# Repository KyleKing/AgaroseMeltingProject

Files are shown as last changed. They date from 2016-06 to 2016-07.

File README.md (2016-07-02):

# Melting Agarose Beads for Enhanced Optical Detection

The goal of this project is to demonstrate that a bead bed of Low Melting Point Agarose beads can capture an analyte with a sandwich immunoassay and when melted, the optical improvement will enhance the detection limit.

In this folder you will find all the code, notes, and resources to help you finish this project. I learned a great deal from electronics and software to microfluidics that I would have never learned in my classes. Feel free to email me any questions [kmking72@gmail.com](mailto:kmking72@gmail.com) or [create a new issue at the private Github repository](https://github.com/KyleKing/AgaroseMeltingProject/issues/new) - note: see login details below for how to access.

I've organized and condensed my notes as concisely as possible. I would start by looking through the posters `1_Posters` to get a general idea of the project.

## How to read `.md` files:

*Summary of this [Stack Overflow answer](http://stackoverflow.com/a/15626336/3219667)*

Download the [Markdown Preview Plus](https://chrome.google.com/webstore/detail/markdown-preview-plus/febilkbfcbhebfnokafefeacimjdckgl) chrome extension. Go to the chrome extensions settings page (*chrome://extensions/*) and check the box to `Allow access to file URL's`. The last step is to go to the [Markdown Preview Plus Settings Panel](chrome-extension://febilkbfcbhebfnokafefeacimjdckgl/options.html) and change the default CSS to `github`.

### Alternatively

The entire folder is on Github under a private repository so you can more easily explore all of the files. You will need the login info for the shared Github account [UMD-MML](https://github.com/UMD-MML) (see the associated Mantis post). Once signed in, visit: https://github.com/KyleKing/AgaroseMeltingProject

# Abstract

Rapid diagnostic platforms have become increasingly necessary to address global disease outbreaks, make informed timely medical decisions, and meet the needs of resource-poor regions. Current diagnostic technology is cost prohibitive for point of care, requiring all samples to be sent to a centralized lab for analysis, which can delay results from several hours to a week. Researchers have attempted to address this issue through the development of microfluidic diagnostics that detect a variety of biomarkers. Many of these tests, however, use two-dimensional surfaces to immobilize target biomarkers, limiting detection performance. Using a three-dimensional biomarker capture matrix will increase the amount of sample fluid in contact with an activated surface by an order of magnitude. This increased contact reduces the diffusion time and leads to faster, more reliable, and more accurate diagnostic tests. Three-dimensional matrices have been considered impractical due to the highly opaque nature of the matrix. I have demonstrated a simple detection method using low melting point (LMP) agarose beads. The beads can be activated to create an exposed biotin group, which can be further activated for a sandiwch immunoassay. While conducting the assay, the agarose beads are nearly opaque; however, once the target biomarkers have been immobilized on the bead matrix, the beads can be melted into a solid mass, reducing light scattering and improving optical clarity for high diagnostic performance. To produce these beads at sufficient scale and throughput, I developed a Raspberry Pi-controlled microfluidic device to automate a scalable production method. With additional research, this novel approach can be developed for clinical applications such as tracking the spread of Ebola, Zika, or other future outbreaks.

## Where is everything?

I packed up everything into a box in the main lab (pictured below). All of the refrigerated chemicals are in the top left drawer of the main lab fridge.

<p align="center">
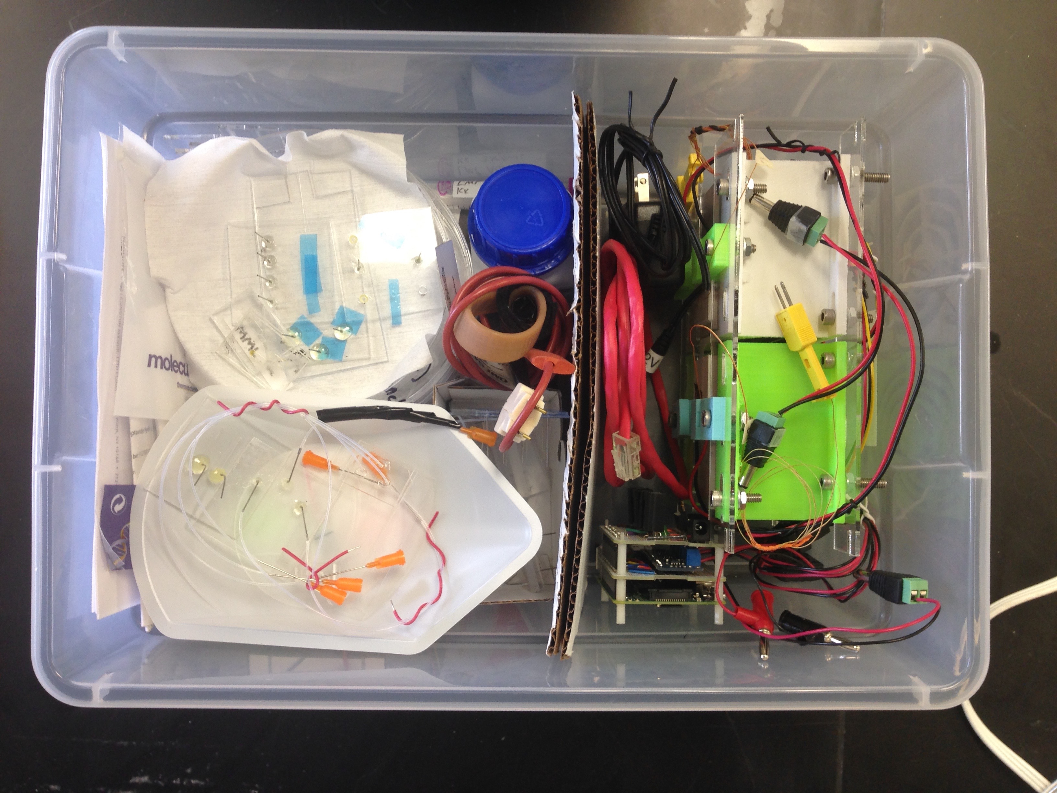
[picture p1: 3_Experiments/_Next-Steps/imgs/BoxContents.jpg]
  
</p>
<p align="center">My box contents</p>

<p align="center">
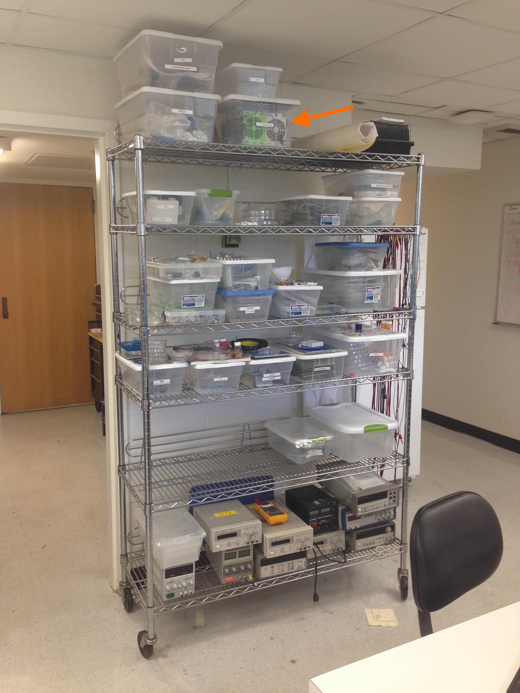
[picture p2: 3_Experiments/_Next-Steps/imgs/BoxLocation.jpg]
  
</p>
<p align="center">The box is located on the top of the shelving unit in the main lab</p>

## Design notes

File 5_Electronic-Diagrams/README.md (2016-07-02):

# Electronic Diagrams

## DIY Version:

Included is a [Fritzing](http://fritzing.org/home/) (`DualHeatStage---Breadboard-Version.fzz`) file for a breaboard version of the dual heat stage electronics (MOSFETs and Thermocouples). The circuit and pin numbers were changed for the soldered version and are included below.

<p align="center">
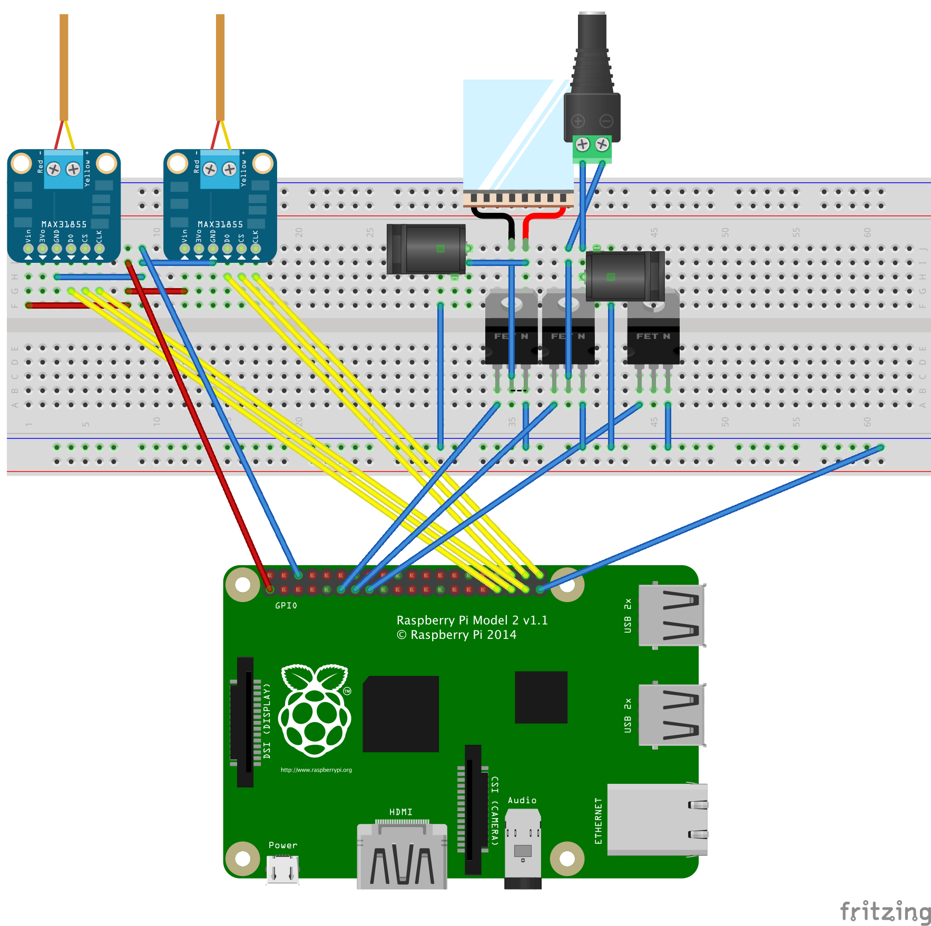
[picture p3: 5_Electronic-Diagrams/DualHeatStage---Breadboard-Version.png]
  
</p>
<p align="center">Fritzing Screenshot</p>

## Soldered Version

Pin Layout - from **Left** (closest to USB ports) to **Right** (closest to microSD slot). To switch between heating and cooling, reverse the leads or flip the tile. For my setup, I kept the bar code side face up.

- MOSFET Pins:
    + Left: 21
    + Middle: 27
    + Right: 23
- Thermocouple Pins
    + Left: pin 21
        * DO pin: 20
        * CS pin: 19
        * CLK pin: 25
    + Middle: pin 27
        * DO pin: 24
        * CS pin: 16
        * CLK pin: 22
    + Right: pin 23
        * DO pin: 18
        * CS pin: 17
        * CLK pin: 4

<p align="center">
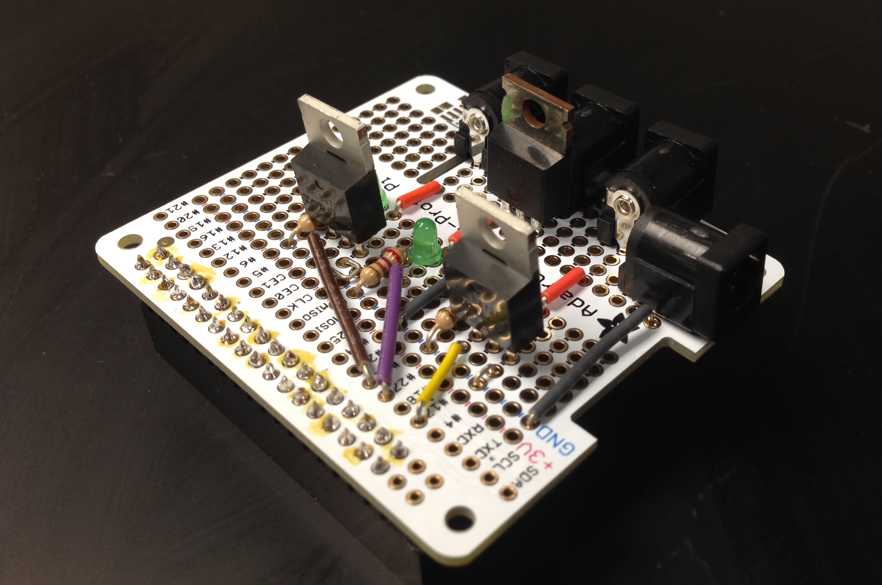
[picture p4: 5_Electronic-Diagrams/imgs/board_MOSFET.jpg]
  
</p>
<p align="center">MOSFET Soldered ProtoBoard</p>

<p align="center">
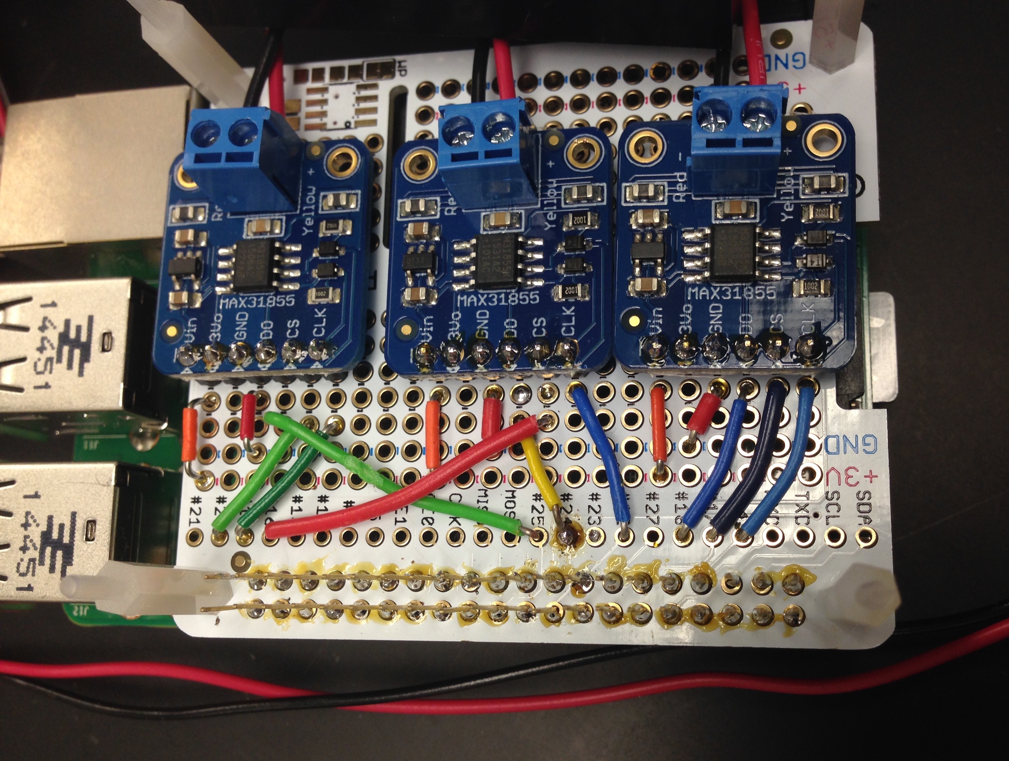
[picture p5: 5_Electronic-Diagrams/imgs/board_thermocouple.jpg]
  
</p>
<p align="center">Thermocouple Soldered ProtoBoard</p>

<p align="center">
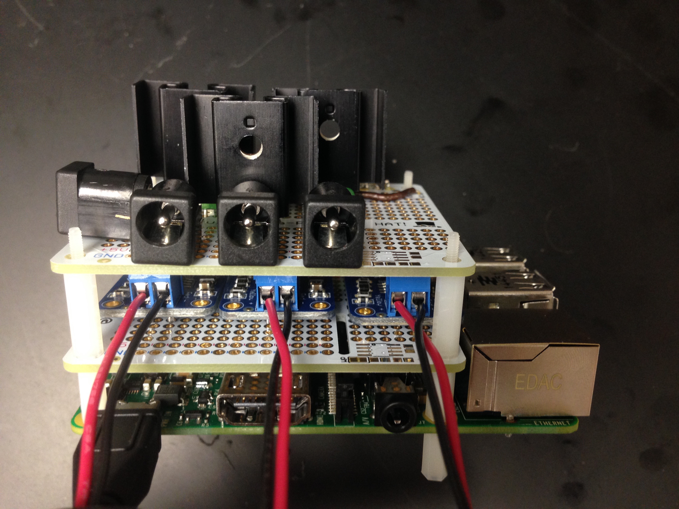
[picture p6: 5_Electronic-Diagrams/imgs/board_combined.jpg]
  
</p>
<p align="center">Side view when both shields are stacked</p>

<p align="center">
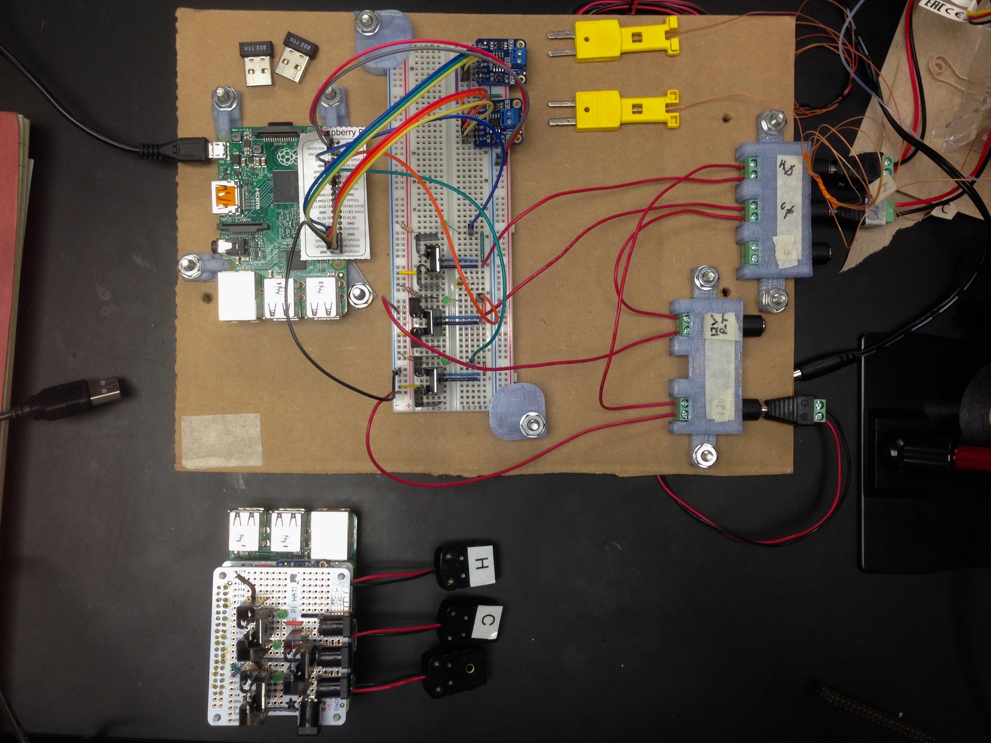
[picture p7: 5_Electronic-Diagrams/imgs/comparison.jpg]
  
</p>
<p align="center">Before and after size comparison</p>

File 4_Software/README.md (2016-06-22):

# Software

Included is the software that controls the Turtlebot and Melter (Single heater/cooler module) - see the folder `MML-HeatStage` for considerably more information. Additionally, I was writing a few MATLAB scripts to automate determining ROI values and shape identification. They have lots of comments and notes, so they are worth improving and looking at it if you want to do something similar.

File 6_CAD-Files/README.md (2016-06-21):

# CAD Files

Explore the sub-folders to see more about the included files. I exported several different formats and the included .stl file is ready to print.

## My 3D printing process:

- Design the part in Autodesk Fusion (Mac) and export a .stl file
- Open the .stl file in Autodesk Meshmixer (free and cross-platform)
- Rotate the 3D object to the best orientation, place on platform, and generate supports
    + You can generate supports in the Makerbot software, but they are difficult to remove. Meshmixer generates far superior supports
- You can submit the .stl file directly at http://ter.ps/3dprinters
    + (Not Recommended) If you print regularly, you can ask for the settings on their printers and submit the .makerbot file directly - which can have a slightly faster turnaround time

## My Laser Cutting Process:

- Start in Autodesk with a 3D model (which makes rounding corners far easier)
- Make a 2D drawing of the design and export as a PDF
- Crop the other lines on the drawing until you can only see the part (in preview on Mac)
- Open the cropped pdf file on a PC and print to 'Microsoft XPS'
    + This step generates a file that the Laser Cutter in the PIRLS lab can recognize. From here you will need to talk to Majid to complete laser cutter training and gain access. Training is only offered once a week and was on a Wednesday morning at like 8 am

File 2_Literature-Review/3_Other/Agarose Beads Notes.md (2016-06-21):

## Paper: Fabrication of superporous agarose beads for protein adsorption: effect of CaCO3 granules content.

Materials: Agarose powder was obtained from Biowest (Shanghai, China). Polyoxyethylene sorbitanmonooleate (Tween 80) was purchased from Dengfeng Chemical (Tianjin, China). Sorbitan trioleate (Span 85) was purchased from China National Pharmaceutical Indus-
try (Beijing, China). Calcium carbonate (CaCO3) granules with an average particle size of 1.05?m and a density of 2.70g/mL were provided by Lihe (Tianjin, China). Metal oxide precursor, titanium(IV) tetraisopropoxide (TTIP, 99%), was purchased from Luchuan Chemical (Shandong, China). Diethylaminoethyl chloride (DEAE-Cl) and bovine serum albumin (BSA) were from Sigma (St. Louis, MO, USA). Other reagents were all of analytical grade and received

Technique:

- 47mL of distilled water plus 3g of agarose powder was heated to 95◦C to prepare an agarose suspension. Agarose concentration in the suspension was 6wt%
- Oil phase consisting of 100mL of cyclohexane, 3.8 g of Span 85 and 1.05 g of Tween 80 was prepared in 250-mL reactor and heated to 60◦C in water bath
- The well-mixed hot agarose suspension was poured into the oil phase under agitation at 1000 rpm. The stirring continued for 30 min, and then the emulsification was rapidly cooled down below 15◦C to solidify the
agarose beads
- The composite beads were collected and washed successively with petroleum ether, ethanol, and water. The beads were wet-screened on 100 mesh and 200 mesh standard sieves and the fraction between the two sieves, about 67%
of total, was collected for further use

## Paper: High-throughput generation of hydrogel microbeads with varying elasticity for cell encapsulation

Materials: Agarose with a gelling temperature in the range of 18e26 ?C (ultra-low gelling temperature agarose)was purchased from SeaPrep (Lonza, Switzerland, www.lonza. com). Phosphate buffer solution (1 wt.%) was purchased from Gibco-BRL (Rockville, MD). A non-ionic surfactant Span-80, mineral oil and glycerol were supplied by Aldridge-Sigma Canada. A 3 wt.% agarose solution was prepared by dissolving 1.5 g of agarose in 48.5 g of a 1 wt.% PBS solution under heating to 70 ?C, and subsequent cooling to room temperature. Agarose solutions with a concentration of 0.5 wt.% were prepared by dilution of the stock solution with a 1 wt.% PBS buffer solution. A non-ionic surfactant Span-80was dissolved to a concentration of 3 wt.% in mineral oil with a viscosity of 30 cPs (Gelest Inc., www.gelest.com).
1.2.

Technique:

- Two agarose solutions with concentrations of 3.0 and 0.5 wt.% were supplied to the two inlets of the MF device using two independently controlled syringe pumps (Harvard Apparatus 33 Dual Syringe Pump, U.S.A.). Later in the text we refer to the solutions with agarose concentration of 3.0 and 0.5 wt.% as to Streams 1 and 2, respectively. Both solutions were heated to 37 ?C by placing the syringe pumps in an oven, however at the point of emulsification their temperature was reduced to 32 ? 1.0 ?C (verified by measuring the temperature with a thermo-couple). The total flow rate of Streams 1 and 2 was Qd ¼ 0.12 mL/h. The solutions were mixed in a serpentine channel with the length of 250 mm (Fig. 1). Thorough mixing of the solution in the wavy channel was verified by introducing a blue food dye in Stream 1 and monitoring the distribution of the dye in the mixed solution along the mixing channel. The concentration of agarose in the droplets was varied by tuning the ratio between the volumetric flow rates of the Streams 1 and 2. At the T-junction, the stream of the mixed agarose solution broke up and released droplets of the mixed agarose solution. The droplets travelled 250 mmin the downstream channel towards the outlet of
the MF device and then exited into an outlet tubing (HPFA tubing, Upchurch Scientific, U.S.A.). The outlet tubing was enclosed by a hose connected to a water circulator cooled to 2 ?C by a 1:4 vol. mixture glycerol and water. The droplets moved through the cooled tubing for approximately 5 min and were collected in a 15 mL conical tube filled with PBS solution. The tube was placed in an ice bath for 45 min to ensure complete gelation of the microgels. The resulting suspension was centrifuged at 1000 rpm at 4 ?C for 5 min, washed with a PBS buffer, and transferred into a PBS buffer.

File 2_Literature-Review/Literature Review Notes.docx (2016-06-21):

# Summary of Current Literature

(Most Relevant Stuff - additional documents in this folder)

## (Fujii paper) A microfluidic device for on-chip agarose microbead generation with ultralow reagent consumption

Link: http://www.ncbi.nlm.nih.gov/pmc/articles/PMC3482248/

Bead size: 20 µm - 55 µm

Device: PDMS

Novelty: “Push-Pull” method on a single chip

Notes:

- This is LMP agarose. I tried replicating it, but could never get it to work

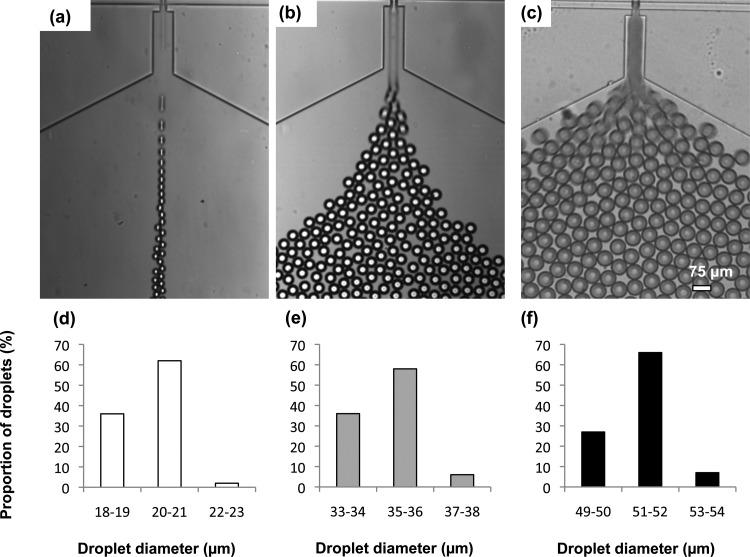
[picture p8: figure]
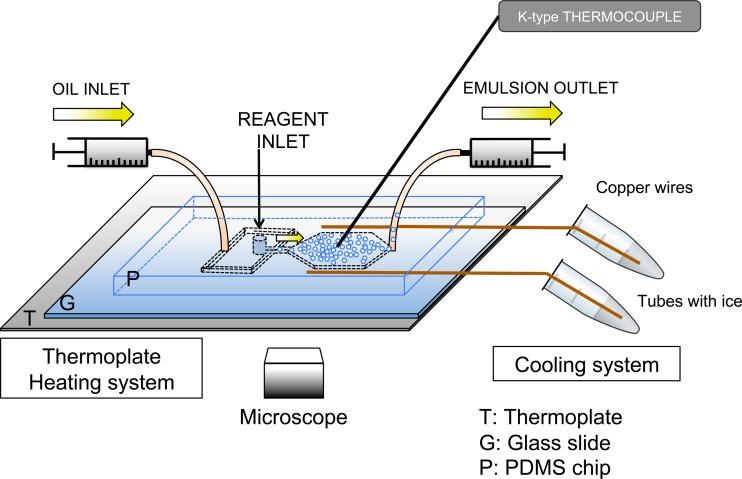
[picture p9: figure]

## High-throughput generation of hydrogel microbeads with varying elasticity for cell encapsulation

Link: http://www.sciencedirect.com/science/article/pii/S0142961210013402

Bead size: 100 µm

Device: PDMS

Novelty: Control elasticity of agarose beads for proper cell expression when encapsulated

Notes:

- Not low melting point agarose
- The dead volume was heated in an oven and the surface of the chip was cooled
- Exit channel was cooled by a water circulator filled with water + glucose at 2°C then were placed in an ice bath for 45 minutes

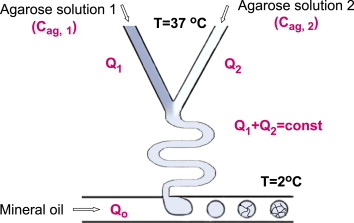
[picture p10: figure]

## Encapsulating bacteria in agarose microparticles using microfluidics for high-throughput cell analysis and isolation

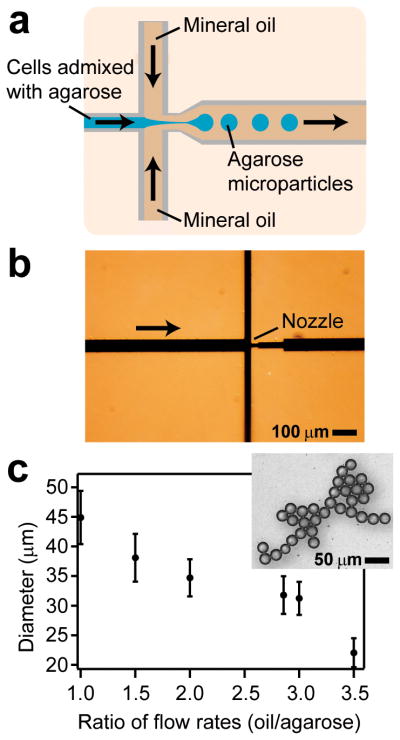
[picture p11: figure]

Link: http://www.ncbi.nlm.nih.gov/pmc/articles/PMC3060957/

Bead size: 22 µm - 45 µm

Device: PDMS

Novelty: PDMS for monodisperse microparticles

Notes:

- Not low melting point agarose
- Heated syringe and device to 40°C
- FACS - high throughput fluorescent bacteria detection system

## Highly Parallel Single-Molecule Amplification Approach Based on Agarose Droplet Polymerase Chain Reaction for Efficient and Cost-Effective Aptamer Selection

Link: http://pubs.acs.org/doi/abs/10.1021/ac2026942

See also:

http://pubs.rsc.org/en/content/articlelanding/2010/lc/c0lc00145g#!divAbstract

And:

http://pubs.acs.org/doi/full/10.1021/ac2033084

Bead size: 40 µm - 120 µm

Device: Glass

Novelty: screening aptamers from ssDNA library by single-molecule emulsion PCR inside of agarose droplets

Notes:

- This is low melting point agarose

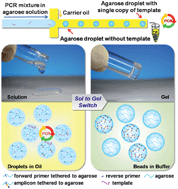
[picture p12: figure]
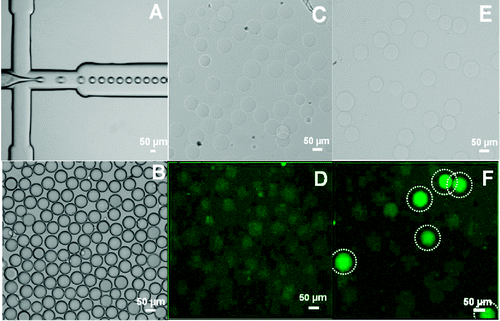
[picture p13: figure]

# Related Literature

Simple method for the production of agarose bioparticles

Link: http://link.springer.com/article/10.1023/A:1008821407995

Novelty: Simple extrusion of agarose + yeast into a cold beaker

Application of gel microdroplet and flow cytometry techniques to selective enrichment of non-growing bacterial cells

Link: https://femsle.oxfordjournals.org/content/197/1/29

Novelty: Flow Cytometry method - (50 µm beads created by membrane emulsion)

Preparation of uniform-sized agarose beads by microporous membrane emulsification technique

Link: http://www.sciencedirect.com/science/article/pii/S0021979707002330

Novelty: membrane emulsification by nitrogen gas (60 µm) - not LMP

Uniform and high throughput agarose gel micro droplet generation device for single cell analysis

Link: https://waseda.pure.elsevier.com/en/publications/uniform-and-high-throughput-agarose-gel-micro-droplet-generation-

Novelty: Very low variation in droplet size (50 µm) for bacteria encapsulation

Fabrication of superporous agarose beads for protein adsorption: effect of CaCO3 granules content.

Link: http://linkinghub.elsevier.com/retrieve/pii/S0021-9673(10)00966-0

Novelty: 50 µm diameter beads produced for chromatography

Drying of Agarose Gel Beads

Link: Springer (http://download.springer.com/static/pdf/388/art%253A10.1007%252FBF02154242.pdf)

Novelty: Slow-drying process with acetone and later crosslinking creates non-porous beads, but increases the melting temperature

Manufacture by water/oil emulsification of porous agarose beads: Effect of processing conditions on mean particle size, size distribution and mechanical properties

Link: http://www.sciencedirect.com/science/article/pii/S0255270105000668

Novelty: Study on the single stirred vessel for agarose bead production ( ≥ 200 µm)

General methods to render macroporous stationary phases nonporous and deformable, exemplified with agarose and silica beads and their use in high-performance ion-exchange and hydrophobic-interaction chromatography of proteins

Link: http://link.springer.com/article/10.1007/BF02290503

Novelty: Drying then crosslinking to remove porous features, but increases melting temperature

Encapsulating Bacteria in Agarose Microparticles Using Microfluidics for High-Throughput Cell Analysis and Isolation

Link: http://pubs.acs.org/doi/full/10.1021/cb100336p

Novelty:

PLGA: http://onlinelibrary.wiley.com/doi/10.1002/app.41566/full (Tm>120°C)

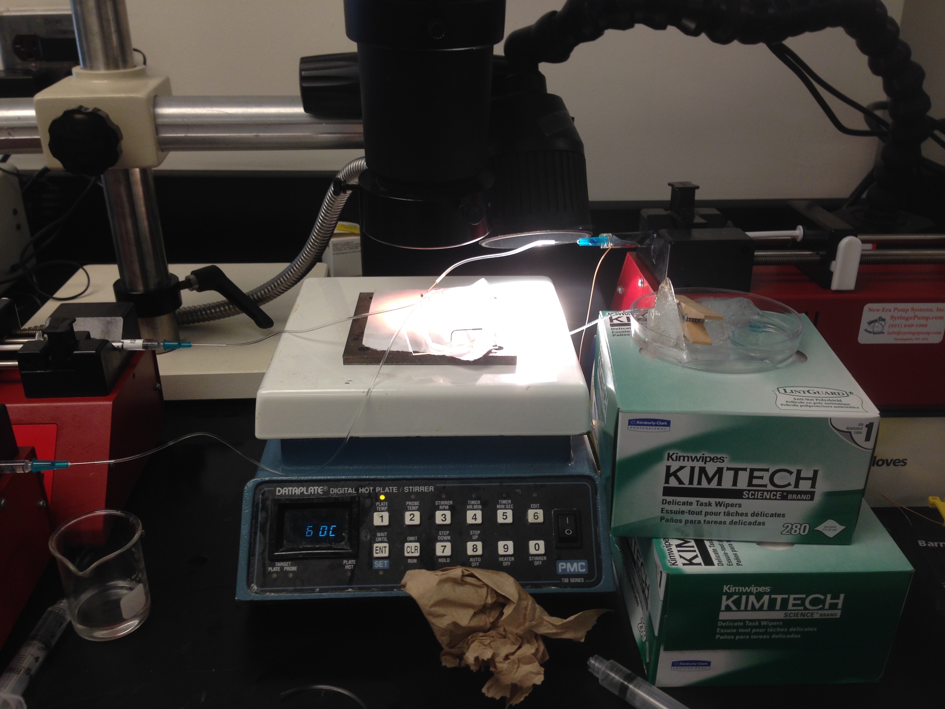
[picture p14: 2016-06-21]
3_Experiments/5_PDMS-Devices/imgs/pressure/newerdevice-overview.jpg

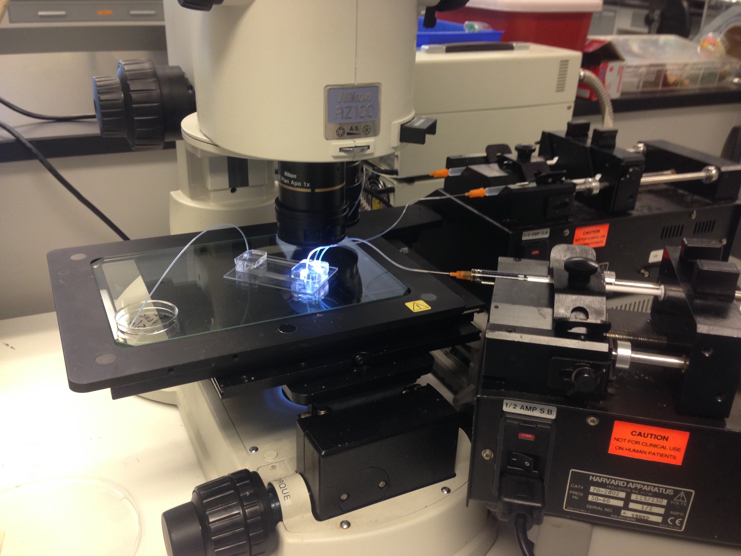
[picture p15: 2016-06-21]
3_Experiments/5_PDMS-Devices/imgs/pressure/needlefreedevice-overview.jpg

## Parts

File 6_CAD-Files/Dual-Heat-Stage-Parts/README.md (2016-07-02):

# Dual Heat Stage Parts (The Turtlebot)

<p align="center">
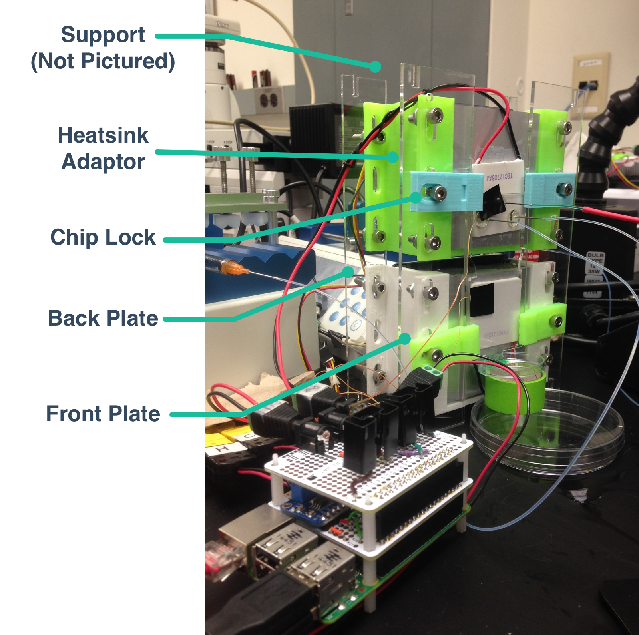
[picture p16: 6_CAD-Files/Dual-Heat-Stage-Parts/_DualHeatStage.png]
  
</p>
<p align="center">Complete Dual Heat Stage (Turtlebot)</p>

<p align="center">
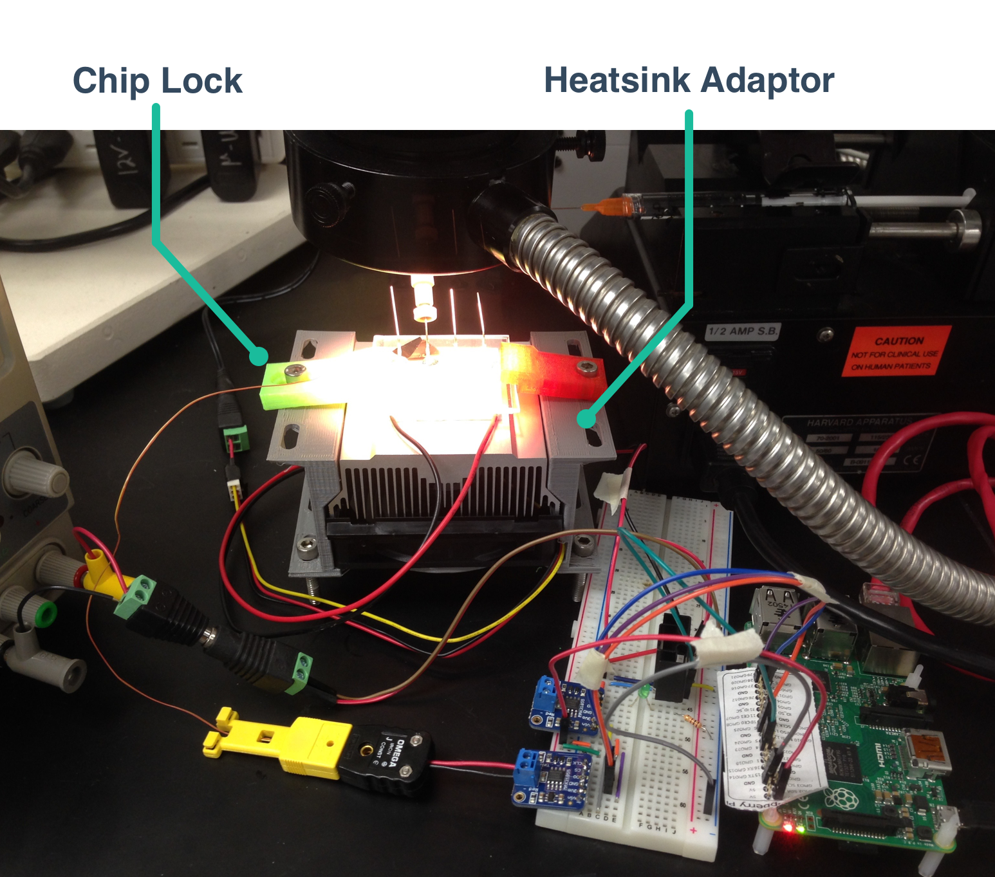
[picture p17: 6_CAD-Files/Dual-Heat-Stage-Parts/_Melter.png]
  
</p>
<p align="center">Single Cooling/Heating Stage (Melter)</p>

<p align="center">
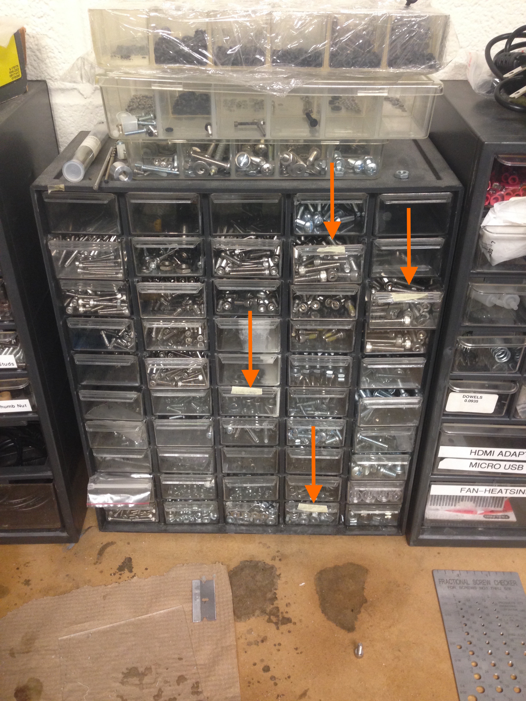
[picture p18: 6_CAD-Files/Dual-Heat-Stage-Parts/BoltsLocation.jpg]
  
</p>
<p align="center">The bolts used are 3/16 - 24 and each drawer of the nuts, washer, and two different length bolts are labeled with masking tape</p>

## Heatsink Adapter

The Turtlebot was designed to be modular. The core component is the heatsink adapter, which has cutouts for the fan wires and bolt locations that allow for finer adjustment. When I left there were a handful printed around lab, so you shouldn't have to print anymore, but if you do there is an included .stl file ready to print.

<p align="center">
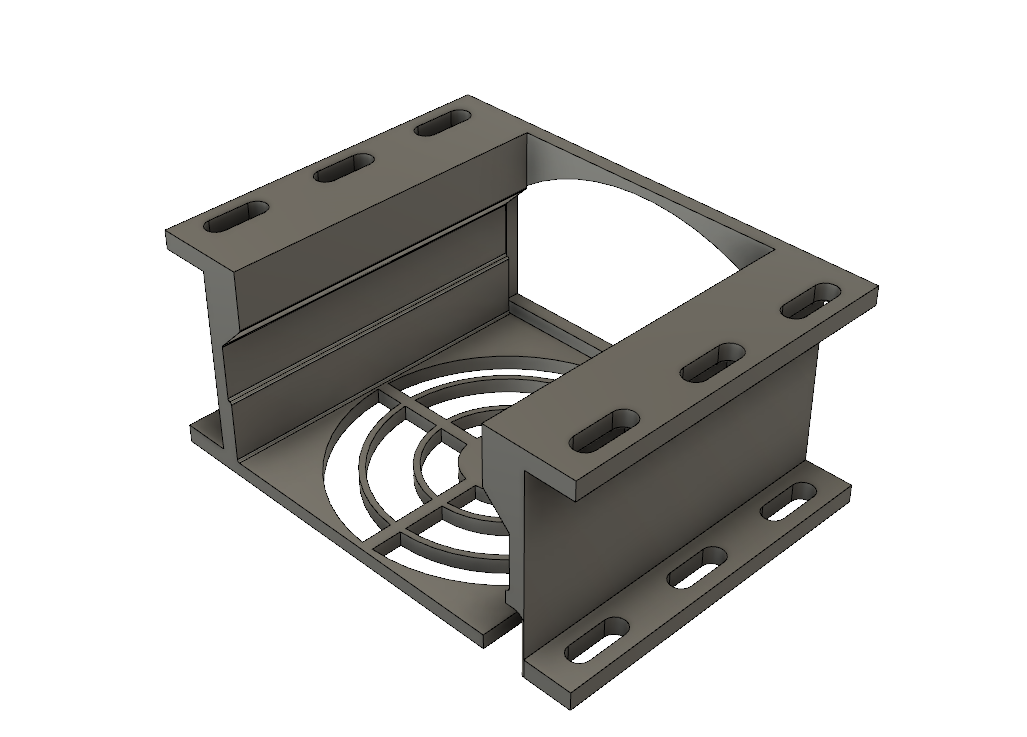
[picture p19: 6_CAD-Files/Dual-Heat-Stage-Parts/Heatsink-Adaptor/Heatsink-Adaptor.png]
  
</p>

<p align="center">The 3D Model</p>

<p align="center">
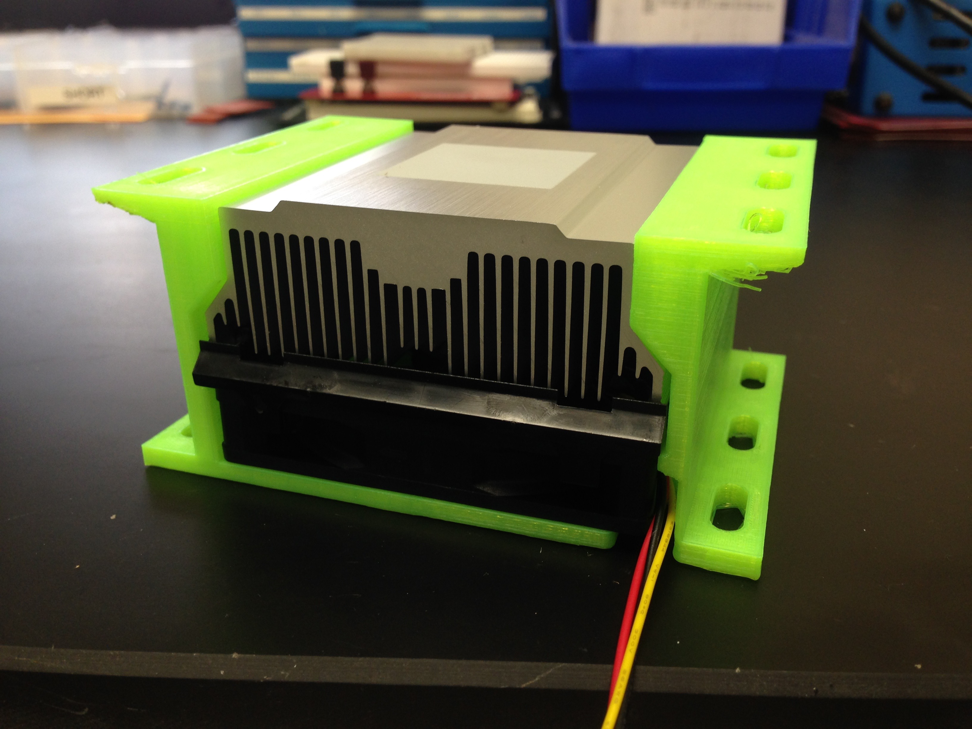
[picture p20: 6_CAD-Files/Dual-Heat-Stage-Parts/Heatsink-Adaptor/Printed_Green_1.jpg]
  
</p>
<p align="center">
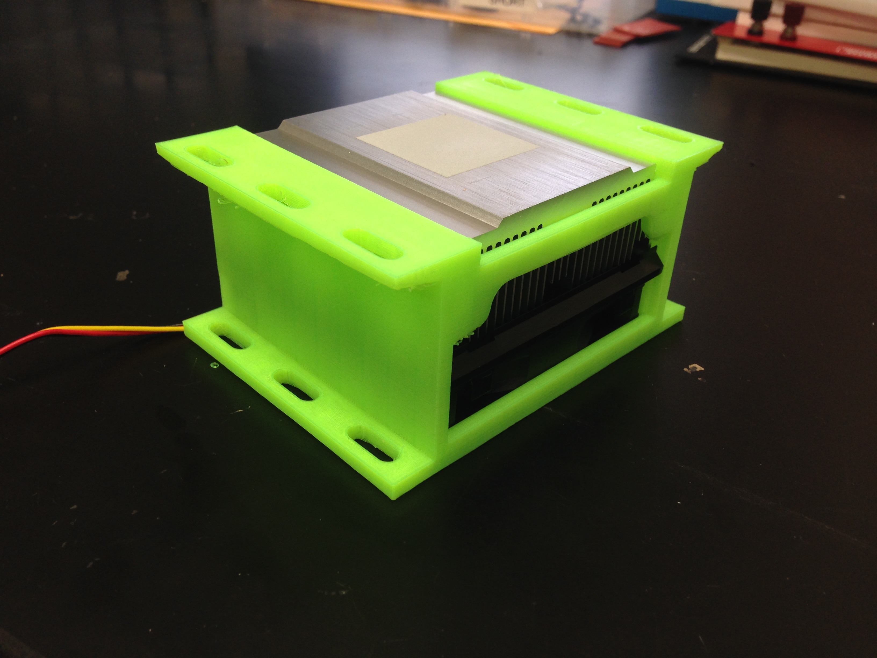
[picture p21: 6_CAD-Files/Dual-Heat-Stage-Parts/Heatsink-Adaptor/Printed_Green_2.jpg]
  
</p>
<p align="center">
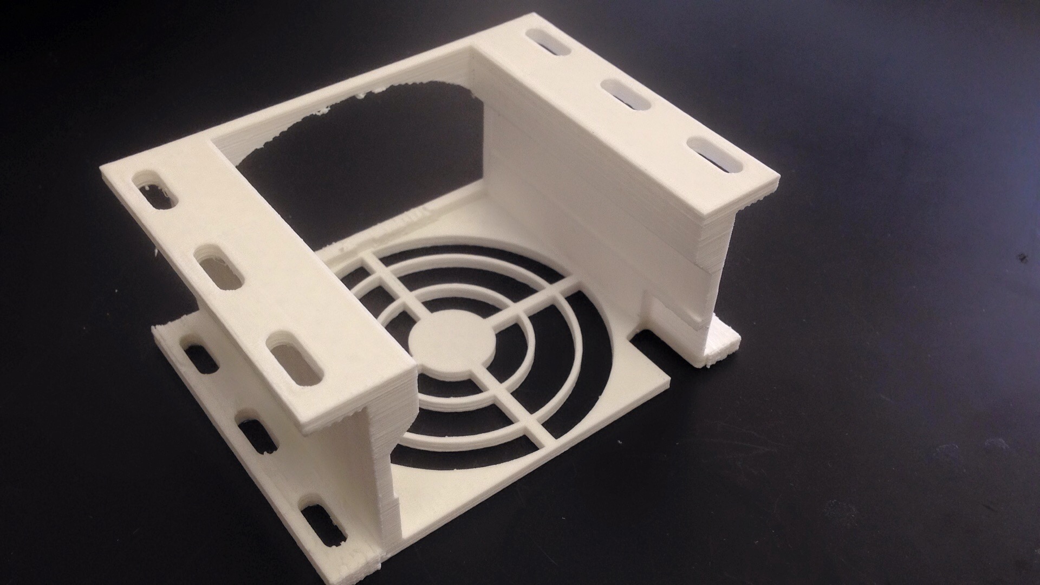
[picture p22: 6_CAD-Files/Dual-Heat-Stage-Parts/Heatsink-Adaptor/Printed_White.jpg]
  
</p>

<p align="center">Printed Versions</p>

## Chip Lock

A much less important piece, this one holds the microfluidic chip in place and allows for a lot of adjustability.

<p align="center">
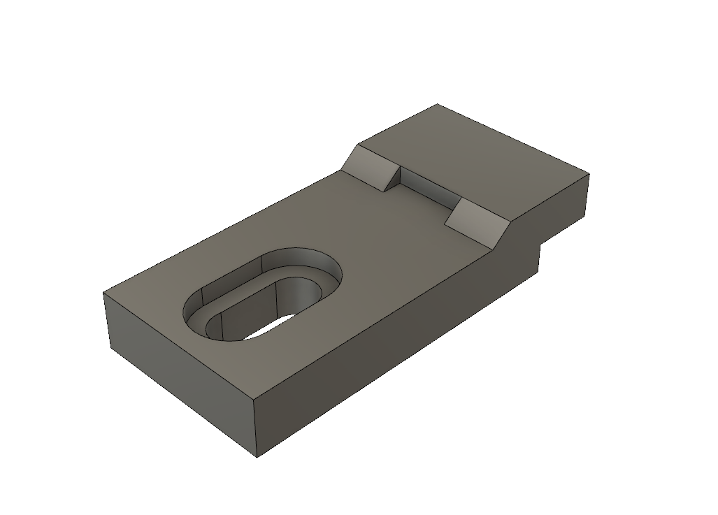
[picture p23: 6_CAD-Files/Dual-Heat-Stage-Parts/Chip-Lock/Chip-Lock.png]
  
</p>

<p align="center">3D model</p>

## Laser Cut Parts

There are three parts included in this folder. Make sure to see the instructions on laser cutting in [the parent folder's README.md file](https://github.com/KyleKing/AgaroseMeltingProject/tree/master/6_CAD%20Files#my-laser-cutting-process)

<p align="center">
  
</p>

<p align="center">One of two back supports</p>

<p align="center">
  
</p>

<p align="center">The front support that keeps the two Peltier tiles from touching</p>

<!-- Support -->

<p align="center">
  
</p>

<p align="center">Optional: if you want to use the dual heat stage horizontally, this provides spacing for airflow behind the fans</p>

<p align="center">
  
</p>

<p align="center">The support part in use. Note the rubber band to hold it in place</p>

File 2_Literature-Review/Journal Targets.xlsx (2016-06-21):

P | Name | Impact Factor | Keywords | Link | Example Paper | Notes | Example Paper | Notes | Example Paper
1 | Journal of Laboratory Automation | 1.87 | improves life sciences R&D (diagnostics). High throughput, micro-technologies, etc. "enable research and development that otherwise would be impossible." | http://jla.sagepub.com | http://jla.sagepub.com/content/20/1/51.full | Miniaturized plate reader for multi-plexing of OD measurements
1 | Sensors | 2.25 | "Sensor applications for food industry, medicine, pharmacy, environmental monitoring, corrosion, etc." - not a great fit | http://www.mdpi.com/journal/sensors/about | http://www.mdpi.com/1424-8220/13/4/5338/htm | Open-Source Colorimeter | http://www.mdpi.com/1424-8220/14/7/11943/htm?sa=X&ved=0CBYQ9QEwAGoVChMIlqiltun8xgIVyzSICh2VJw1- | A Low-Cost Real Color Picker Based on Arduino | http://www.mdpi.com/1424-8220/11/6/5754/htm | Microfluidics-Based Lab-on-Chip Systems in DNA-Based Biosensing: An Overview
1 | Instrumentation, Science, and Technology | 0.53 |  | http://www.tandfonline.com/toc/list20/current]
2 | Modern Instrunmentation | 0.14
2 | Sensors and Actuators B: Chemical | 4.1 | μTAS, Signal processing, biomedical applications, etc. | http://www.journals.elsevier.com/sensors-and-actuators-b-chemical | http://www.sciencedirect.com/science/article/pii/S0925400511003881 | An integrated microfluidic system for fast, automatic detection of C-reactive protein | http://www.sciencedirect.com/science/article/pii/S0925400506004485 | Integrated microfluidic systems for automatic glucose sensing and insulin injection | http://www.sciencedirect.com/science/article/pii/S0925400511010859 | Centrifugal microfluidic platform for rapid PCR amplification using integrated thermoelectric heating and ice-valving
3 | Something for IEEE ...? | 2.48 | The linked journal is mostly interested in implantable devices... | http://ieeexplore.ieee.org/xpl/topAccessedArticles.jsp?punumber=4156126&topArticlesDate=February+2016 | http://ieeexplore.ieee.org/xpls/abs_all.jsp?arnumber=6189895&tag=1 | Automatic control for laboratory sterilization process based on arduino hardware
3 | Electropheresis | 3.02 | Related to this paper, but not much else -> | http://onlinelibrary.wiley.com/journal/10.1002/(ISSN)1522-2683 | http://onlinelibrary.wiley.com/doi/10.1002/elps.201400128/full | Getting started with open-hardware: Development and control of microfluidic devices | http://onlinelibrary.wiley.com/doi/10.1002/anie.201501618/full | Machine-Assisted Organic Synthesis (Not main journal)
3 | Biosensors and Bioelectronics | 6.45 | " biological materials and designs in novel diagnostic and electronic devices including sensors, DNA chips, electronic noses, lab-on-a-chip and μ-TAS." and "provide important insights into the practical application, manufacture and commercialisation of biosensors and bioelectronics." | http://www.sciencedirect.com/science/journal/09565663 | http://www.sciencedirect.com/science/article/pii/S0956566314007489 | A portable low-cost long-term live-cell imaging platform for biomedical research and education | -> | See photo! | http://www.sciencedirect.com/science/article/pii/S0956566305002927 | Miniaturized immunoassay microfluidic system with electrokinetic control
3 | Engineering Science and Technology, an International Journal |  | "Biomedical Engineering and Instrumentation; Coding, etc." | http://www.journals.elsevier.com/engineering-science-and-technology-an-international-journal | http://www.sciencedirect.com/science/article/pii/S2215098615303220 | Microcontroller USB interfacing with MATLAB GUI for low cost medical ultrasound scanners
5 | Journal of Biological Methods |  | More methods-based in the development of protocols | http://www.jbmethods.org/jbm/index | http://www.ncbi.nlm.nih.gov/pmc/articles/PMC4598940/ | Open source and DIY hardware for DNA nanotechnology labs
x | Applied Physics Letters |  |  | http://scitation.aip.org/content/aip/journal/apl | http://scitation.aip.org/content/aip/journal/apl/102/19/10.1063/1.4807118 | DropBot: An open-source digital microfluidic control system
x | EPJ Techniques and Instrumentation (TI) |  |  |  | http://epjtechniquesandinstrumentation.springeropen.com/articles/10.1140/epjti/s40485-014-0009-z | Paper using an Arduino for control
x | Journal of Biological Engineering |  | Only interested in synthetic biology, education, or bioproduction... | http://jbioleng.biomedcentral.com | http://jbioleng.biomedcentral.com/articles/10.1186/s13036-016-0024-5 | End-to-end automated microfluidic platform for synthetic biology: from design to functional analysis



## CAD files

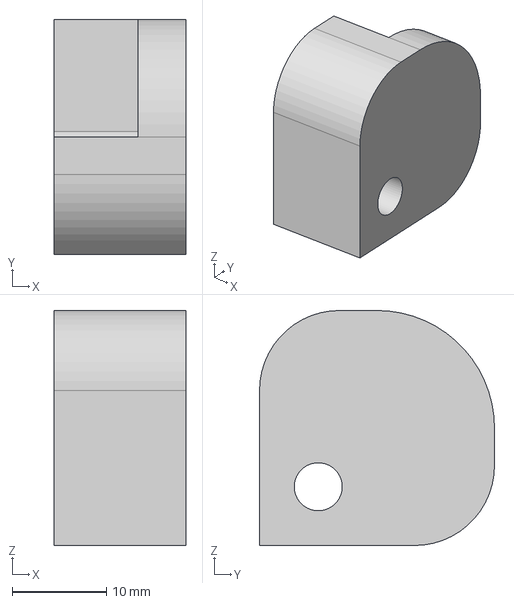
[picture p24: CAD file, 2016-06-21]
6_CAD-Files/Cardboard-Platform-Parts/Breadboard-Mount/Breadboard-Mount.step
14.0 x 25.0 x 25.0 mm

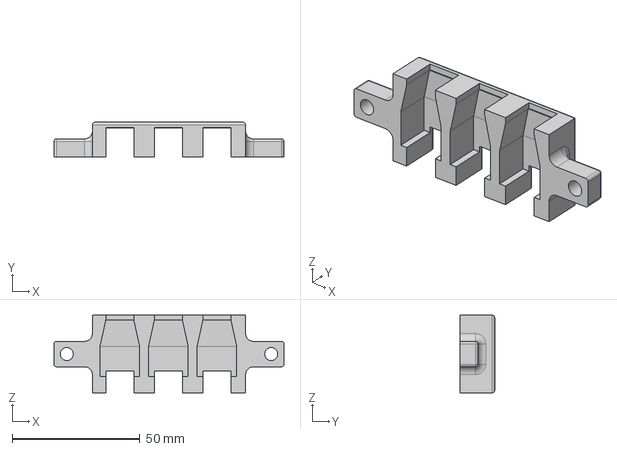
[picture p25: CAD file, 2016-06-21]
6_CAD-Files/Cardboard-Platform-Parts/DC-Jack-Hookup-Mount/DC-Jack-Hookup-Mount.step
90.0 x 13.5 x 30.5 mm

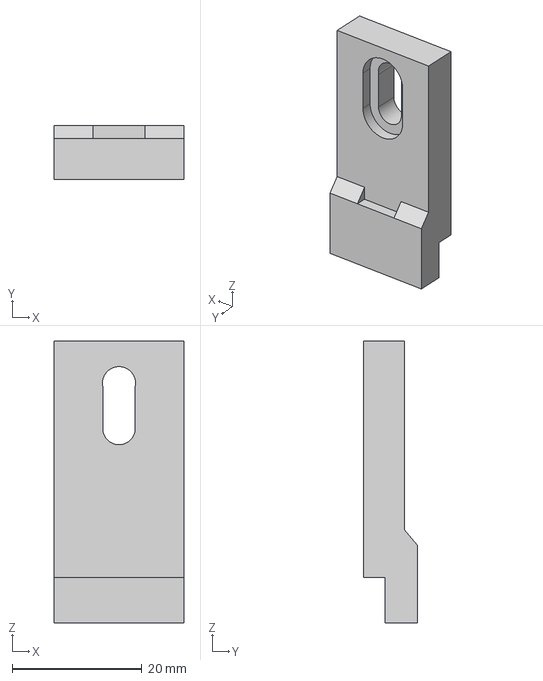
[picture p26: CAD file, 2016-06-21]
6_CAD-Files/Dual-Heat-Stage-Parts/Chip-Lock/Chip-Lock.step
20.0 x 8.30 x 43.5 mm

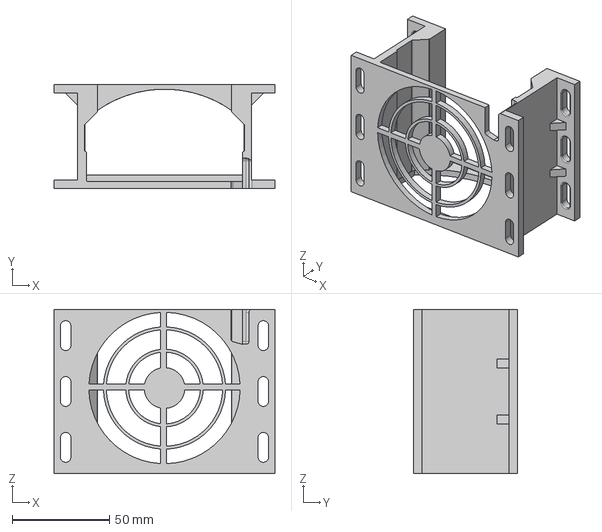
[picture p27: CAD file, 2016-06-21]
6_CAD-Files/Dual-Heat-Stage-Parts/Heatsink-Adaptor/Heatsink-Adaptor.step
113.9 x 53.6 x 84.6 mm

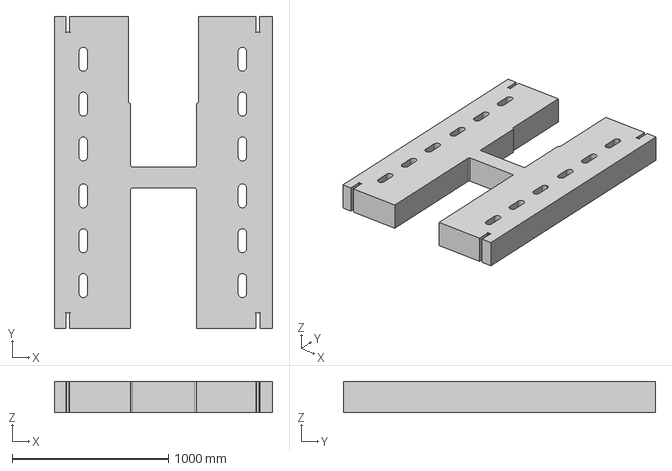
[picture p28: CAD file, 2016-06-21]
6_CAD-Files/Dual-Heat-Stage-Parts/Laser-Cut-Parts/Front.step
1400.0 x 2000.0 x 200.0 mm

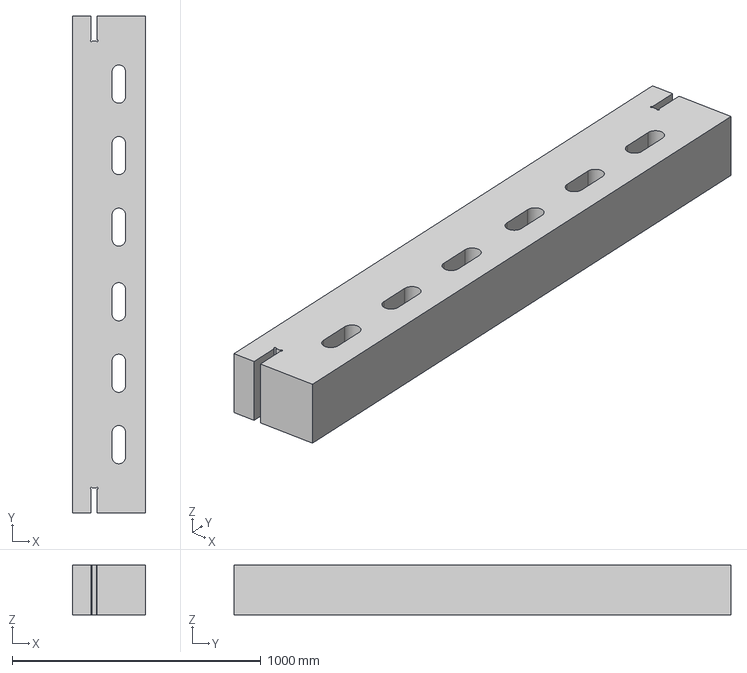
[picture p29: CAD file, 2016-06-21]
6_CAD-Files/Dual-Heat-Stage-Parts/Laser-Cut-Parts/Back.step
293.0 x 2000.0 x 200.0 mm

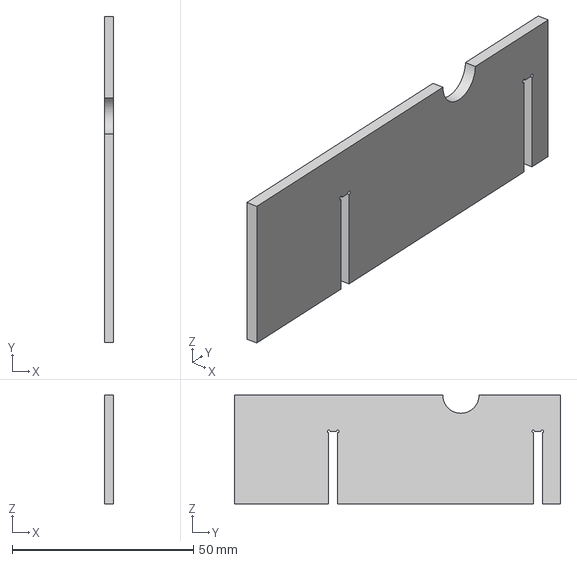
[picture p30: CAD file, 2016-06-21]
6_CAD-Files/Dual-Heat-Stage-Parts/Laser-Cut-Parts/Support.step
2.40 x 90.0 x 30.0 mm

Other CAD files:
6_CAD-Files/Cardboard-Platform-Parts/Breadboard-Mount/Breadboard-Mount.f3d
6_CAD-Files/Cardboard-Platform-Parts/Breadboard-Mount/Breadboard-Mount.iges
6_CAD-Files/Cardboard-Platform-Parts/DC-Jack-Hookup-Mount/DC-Jack-Hookup-Mount.f3d
6_CAD-Files/Cardboard-Platform-Parts/DC-Jack-Hookup-Mount/DC-Jack-Hookup-Mount.iges
6_CAD-Files/Dual-Heat-Stage-Parts/Chip-Lock/Chip-Lock.f3d
6_CAD-Files/Dual-Heat-Stage-Parts/Chip-Lock/Chip-Lock.iges
6_CAD-Files/Dual-Heat-Stage-Parts/Chip-Lock/Chip-Lock.stl
6_CAD-Files/Dual-Heat-Stage-Parts/Heatsink-Adaptor/Heatsink-Adaptor.f3d
6_CAD-Files/Dual-Heat-Stage-Parts/Heatsink-Adaptor/Heatsink-Adaptor.iges
6_CAD-Files/Dual-Heat-Stage-Parts/Laser-Cut-Parts/Back.f3d
6_CAD-Files/Dual-Heat-Stage-Parts/Laser-Cut-Parts/Back.iges
6_CAD-Files/Dual-Heat-Stage-Parts/Laser-Cut-Parts/Front.f3d
6_CAD-Files/Dual-Heat-Stage-Parts/Laser-Cut-Parts/Front.iges
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

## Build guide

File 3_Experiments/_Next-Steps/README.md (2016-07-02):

# Next Steps

So far the droplet generator works relatively well. The challenge has been to load a bead bed with the agarose beads. I've taken a couple of different approaches and looked into filtering, pre-packing the beads (silica glass beads to *seed* the bead bed), or using wells instead of a bead bed, but ran out of time to pursue these options.

I would suggest to look through literature and determine how researchers use agarose beads in filtration columns and other similar applications. Additionally, it may be worth considering a different hydrogel or adding a copolymer to the agarose beads (where both scenarios the melting temperature stays under 100°C).

To generate beads, you will need to mill a new chip. I was creating larger, plug flow droplets with the final device, but you will want to return to the optimal size droplets. Instead of making the entire exit channel the same width (~100 µm), use a larger bit (~150-200 µm) for the final 40 mm of the exit channel. You don't want to go any larger than twice the thinner section or the beads will be more likely to coalesce at the width change.

Once the bead packing step has been figured out and prototyped on the Melter heat stage, the next direction is to integrate a Fluorine-doped tin oxide (FTO) coated glass plate bonded to a PMMA chip with the microfluidic features and ports. This way the beads can be easily melted with very little energy (great for portability) and a transmission optical assay is possible.

## Where is everything?

I packed up everything into a box in the main lab (pictured below). All of the refrigerated chemicals are in the top left drawer of the main lab fridge.

<p align="center">
  
</p>
<p align="center">My box contents</p>

<p align="center">
  
</p>
<p align="center">The box is located on the top of the shelving unit in the main lab</p>

<p align="center">
  
</p>
<p align="center">The bolts used are 3/16 - 24 and each drawer of the nuts, washer, and two different length bolts are labeled with masking tape</p>

<p align="center">
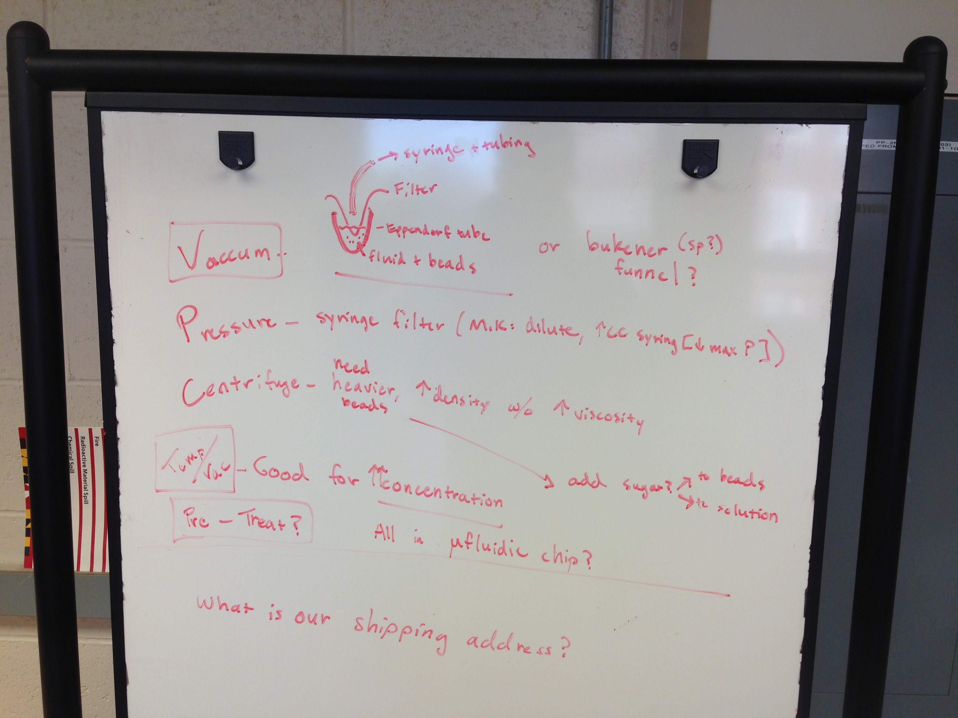
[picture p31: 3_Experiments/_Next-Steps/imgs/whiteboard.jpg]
  
</p>
<p align="center">A few notes about potential agarose bead filtration/concentration strategies</p>

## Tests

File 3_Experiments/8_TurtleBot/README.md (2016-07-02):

# Turtlebot (dual heat stage)

I had too much fun working on the Raspberry Pi and building this device that I got sidetracked from the actual project. At this point this device should be entirely self-contained and can be modified however you need to. There are three parts. first the CAD for the 3D printed parts (`see 6_CAD-Files`). Second, the electronics, which are described in more detail under the folder, `5_Electronic-Diagrams`. Third, the code, see `4_Software/MML-HeatStage` for instructions and additional information. This README will only cover the history of the device and some setup pictures for reference.

## Manually Controlled Version

This version was the first demonstration and was kluged together. The device worked surprisingly well, but needed constant oversight.

<p align="center">
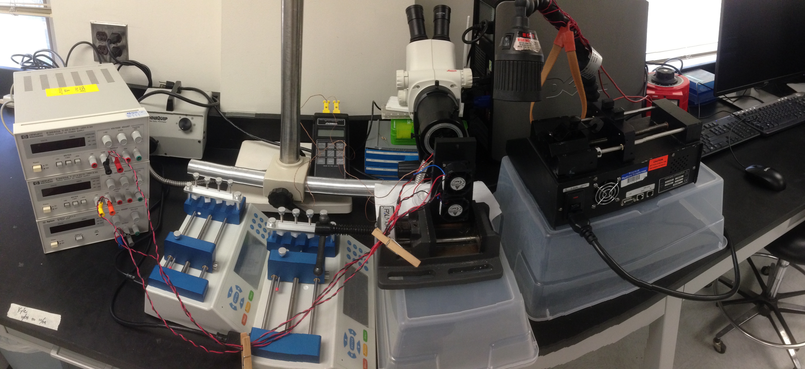
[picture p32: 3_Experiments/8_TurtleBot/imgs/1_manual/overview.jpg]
  
</p>
<p align="center">
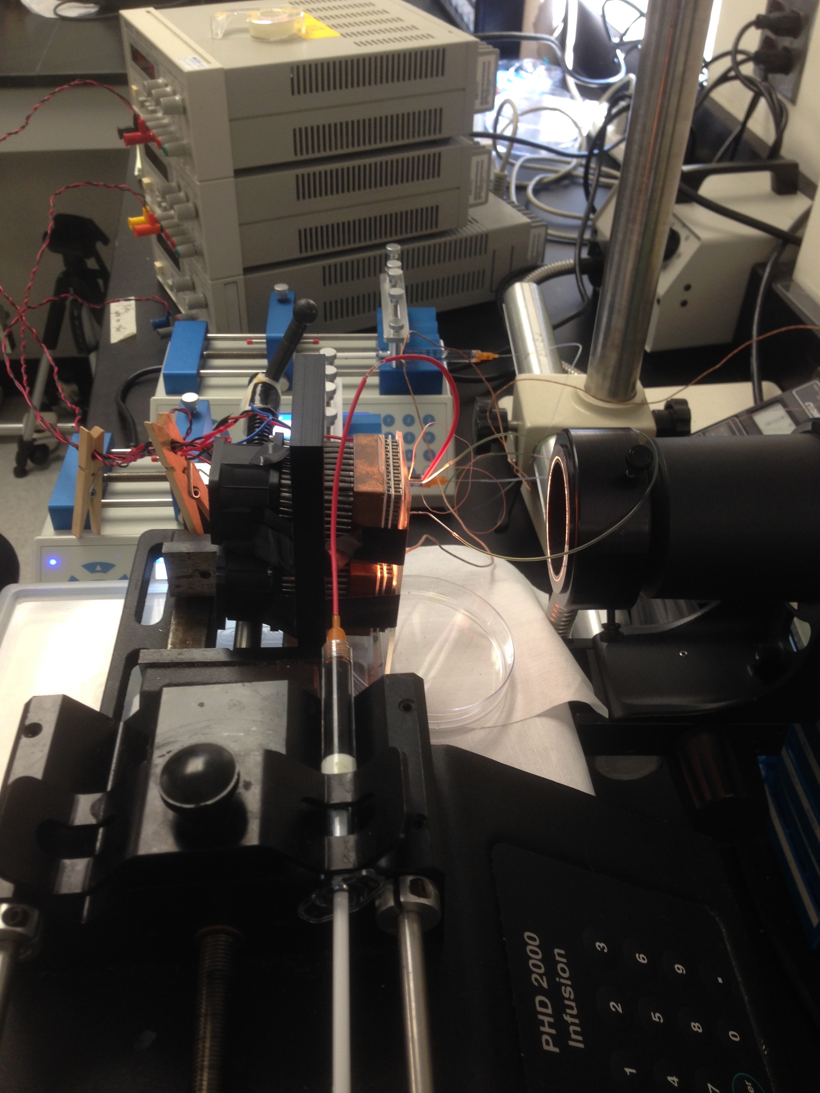
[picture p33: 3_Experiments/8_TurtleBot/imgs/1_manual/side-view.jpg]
  
</p>
<p align="center">Original device setup</p>

<p align="center">
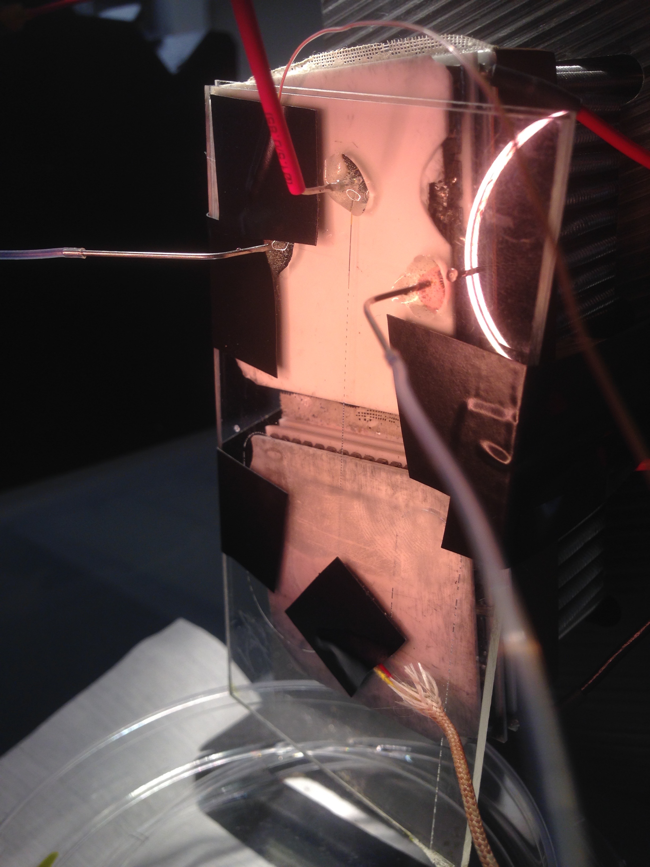
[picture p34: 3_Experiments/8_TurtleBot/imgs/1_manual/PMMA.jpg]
  
</p>
<p align="center">The PMMA device and camera setup</p>

<p align="center">
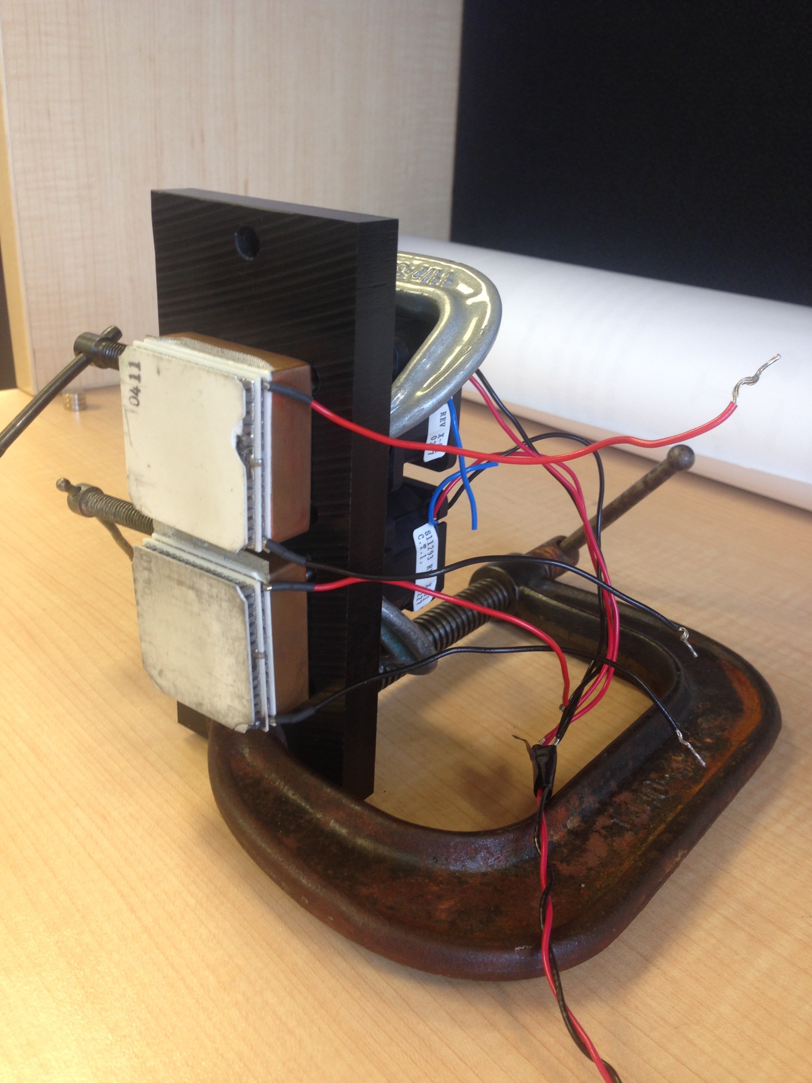
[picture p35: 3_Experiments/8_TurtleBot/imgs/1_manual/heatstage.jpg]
  
</p>
<p align="center">The first dual heat stage</p>

<p align="center">
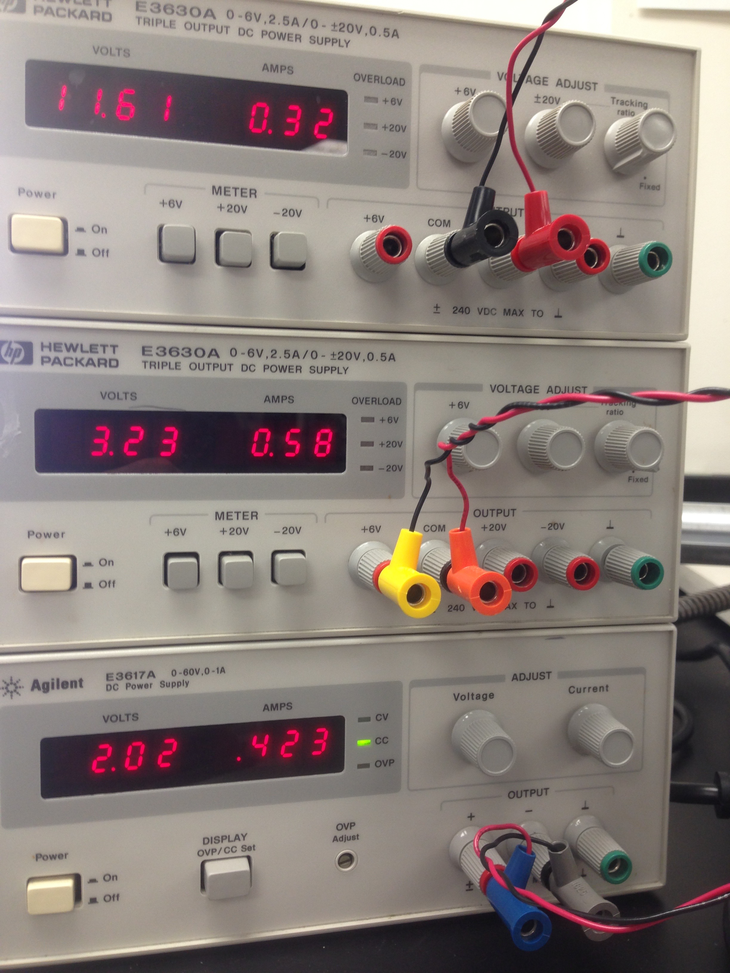
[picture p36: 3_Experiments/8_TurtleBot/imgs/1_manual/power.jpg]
  
</p>
<p align="center">Manually monitored power supply</p>

## Improvements

Attempting to automate the device and add controls, while improving the heat stage, I began ordering parts and testing out design changes:

<p align="center">
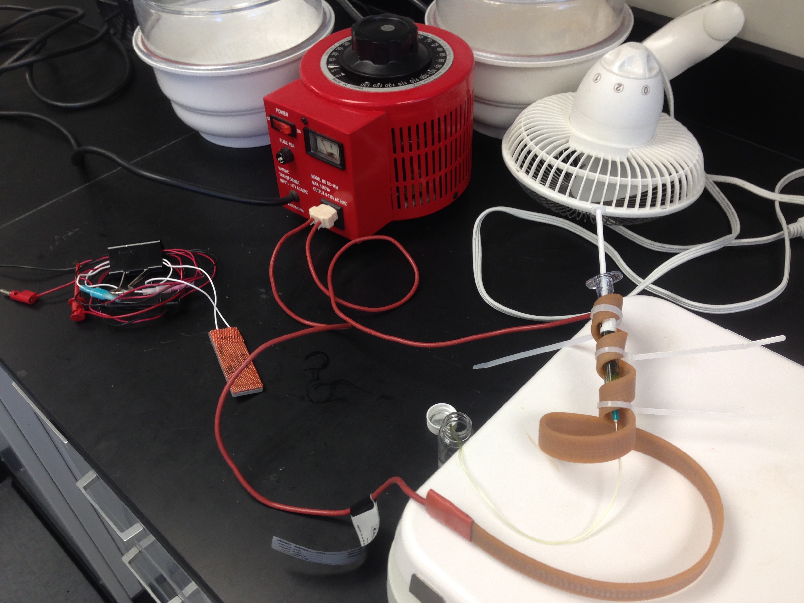
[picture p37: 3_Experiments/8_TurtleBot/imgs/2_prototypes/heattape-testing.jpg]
  
</p>
<p align="center">
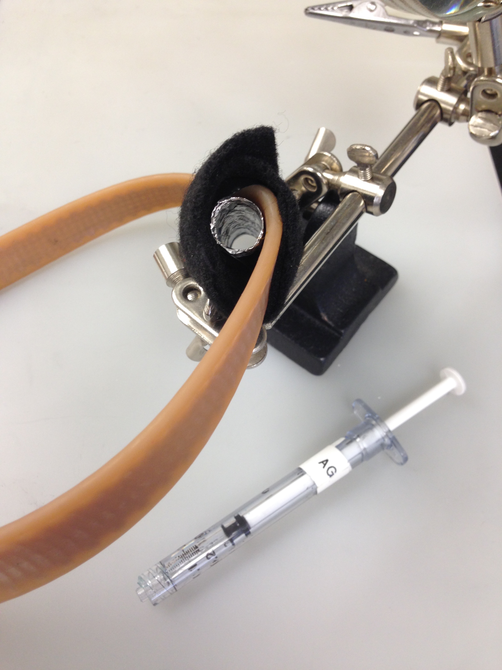
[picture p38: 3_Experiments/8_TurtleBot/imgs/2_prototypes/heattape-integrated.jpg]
  
</p>
<p align="center">First I designed a better syringe heater using aluminum foil (to cast the shape of the syringe), heat tape, black felt for insulation (to protect the syringe pump), and plenty of electrical tape for mechanical strength</p>

<p align="center">
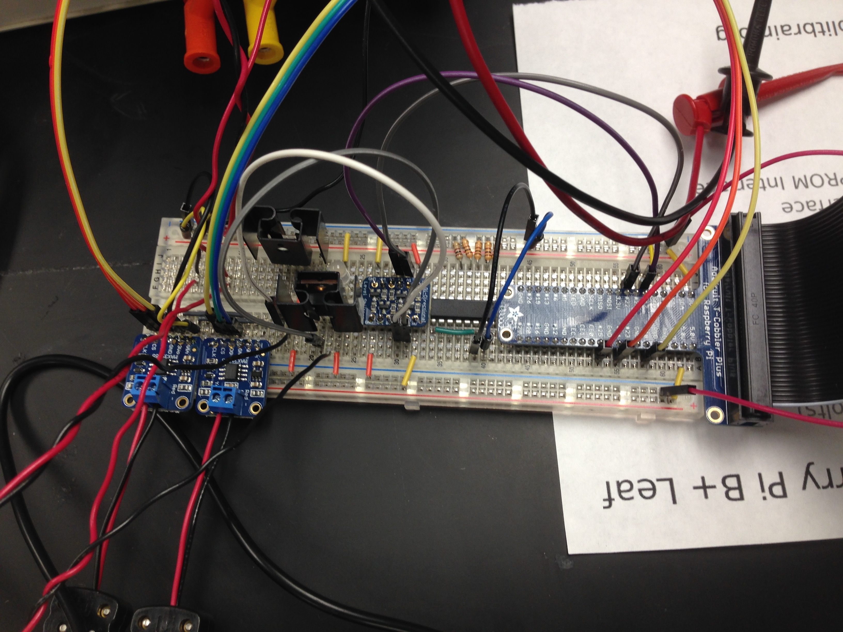
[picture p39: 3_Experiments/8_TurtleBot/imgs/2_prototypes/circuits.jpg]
  
</p>
<p align="center">
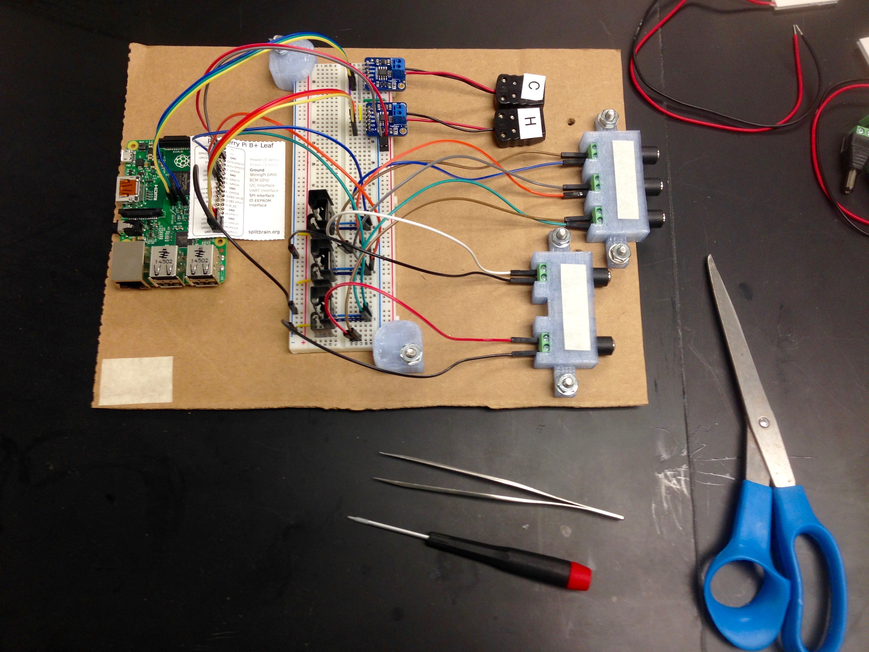
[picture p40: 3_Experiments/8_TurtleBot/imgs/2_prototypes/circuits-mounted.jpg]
  
</p>
<p align="center">To obtain automated control, I had to play around with the electrical components. To finalize the circuit and skip the lengthy process of soldering, I mounted all of the components securely to a piece of cardboard (or it could have been a piece of plastic)</p>

<p align="center">
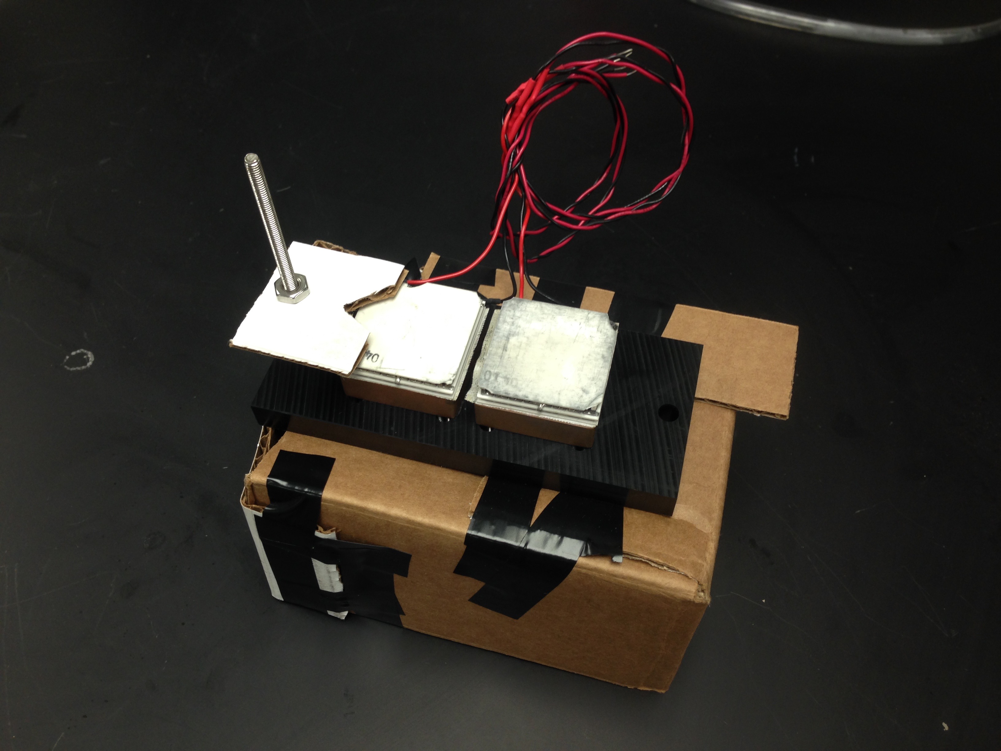
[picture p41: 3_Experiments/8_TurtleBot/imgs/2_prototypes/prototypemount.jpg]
  
</p>
<p align="center">
  
</p>
<p align="center">The heat stage also got a face lift. Based on the cardboard prototype, I designed a 3D printed version that could be modularly assembled and disassembled</p>

## Final Version

Collecting all of the design improvements and modifications, i assembled a final device that could be interchangeably used for various projects.

<p align="center">
  
</p>
<p align="center">An early setup using the cardboard-mounted electronics and early versions of the controller code</p>

<p align="center">
  
</p>
<p align="center">The final setup with the soldered electronic controls and compact setup</p>

<p align="center">
  
</p>
<p align="center">The bolts used are 3/16 - 24 and each drawer of the nuts, washer, and two different length bolts are labeled with masking tape</p>

<p align="center">
  
</p>
<p align="center">A quick candid photo of the device in use</p>

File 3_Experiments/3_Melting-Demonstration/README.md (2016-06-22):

# Melting Tests (Proof of Concept)

Both of the melting tests showed that possibility of this approach to optical improvement.

## Bulk Demonstration

The bulk beads were placed into large PDMS wells. The beads melted around 80°C, which is below the glass transition temperature of PMMA and COC. Even with one bead, the optical improvement is visible.

Download the complete video: `MeltingLMPGel.mp4`

## Miniature Beads

The beads produced from the PMMA device were loaded as a bead bed. Notably the beads were difficult to pack. I initially attributed the difficult to clogging in the exit channel and the lack of concentrated beads; however, this may have been the beads collapsing in the channel under the static pressure. Additionally, the water boiled off of the device as you can see the food dye flow out the entrance. Make sure to purge the bead bed before melting.

<p align="center">
  
  <!-- <figcaption style="text-align: center;">The bead bed before melting step (see video: `PMMA Device Beads/Melting.mov`)</figcaption> -->
</p>

<p align="center">The bead bed before melting step (see video: `PMMA Device Beads/Melting.mov`)</p>

<p align="center">
  
  <!-- <figcaption style="text-align: center;">The bead bed after melting step</figcaption> -->
</p>

<p align="center">The bead bed after melting step</p>

See the complete video: `BeadBedMelt.mp4`

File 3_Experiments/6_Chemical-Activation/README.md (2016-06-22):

# Chemical Activation

I did a pretty wide literature review and settled on two approaches. The first was a formaldehyde sensor, which I liked the simplicity, but when heated the reaction progresses so it just blackens and any optical improvement is obscured. The second approach using a hydrazide was far more effective. I made a proof of concept demonstration using bulk beads (~1 mm diameter).

## Agarose Formaldehyde Sensor (Tollens Reagent)

<p align="center">
  
</p>

<p align="center">I demonstrated concentration dependence over an arbitrary range</p>

<p align="center">
  
</p>

<p align="center">Then I setup to do a melting demonstration. Before the melt the beads were a light brown color</p>

<p align="center">
  
</p>

<p align="center">However, after melting the color became a burnt black. The heat had driven the reaction to completion</p>

See the complete video: `TollensReagentMeltTest.mp4`

## Agarose Direct Assay / Sandwich Immunoassay

The agarose beads are incubated with sodium periodate, then a streptavidin-hydrazide complex, leaving two active streptavidin sites per monomer for biotin-avidin binding.

<p align="center">
  
</p>
<p align="center">Reaction 1</p>

<p align="center">
  
</p>
<p align="center">Reaction 2</p>

For more specifics, refer to the entire protocol: `2_Hydrazide-Reaction/ElicellProtocol.pdf` or the two related papers: [EliCell assay for the detection of released cytokines from eosinophils](http://www.sciencedirect.com/science/article/pii/S0022175903000760) and [EliCell: a gel-phase dual antibody capture and detection assay to measure cytokine release from eosinophils](http://www.sciencedirect.com/science/article/pii/S0022175900002647)

# Demonstration

I demonstrated the Hydrazide-activation assay using a direct assay (the exposed streptavidin on the agarose beads - biotion/gold). The visible rosy red color is from the gold nanoparticles. After heating there is an optical improvement and the color difference is visibly noticeable between the controls.

<p align="center">
  
</p>
<p align="center">Analysis</p>

<p align="center">
  
</p>

<p align="center">The beads used were from agarose poured into the plate below and then scraped off (Macro-Scale Bead Plate)</p>

<p align="center">
  
</p>
<p align="center">PDMS Wells - the beads were then placed into this PDMS plate bonded to a glass backing for analysis</p>

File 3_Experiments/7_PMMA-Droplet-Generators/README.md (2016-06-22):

# PMMA Droplet Generator Devices

After some success with the PDMS devices, I explored alternatives using CNC-milled PMMA. This is a short summary of the considered designs and relative success of each.

<!-- MarkdownTOC depth="6" autolink="true" bracket="round" -->

- [General Overview](#general-overview)
  - [Milling](#milling)
  - [Bonding](#bonding)
  - [Needle Press](#needle-press)
- [Evolution of the PMMA Devices](#evolution-of-the-pmma-devices)

<!-- /MarkdownTOC -->

## General Overview

The devices were milled on the CNC and the included g-code files will make producing additional chips very easy. My general process is described below.

<p align="center">
  
</p>
<p align="center">Aligning the CNC</p>

### Milling

- Cut a PMMA chip to 50mm x 100mm and cut a notch at the end (the PMMA with the blue protective tape)
- Cut a second PMMA piece to the same dimensions, but with the thinner PMMA stock material (brown protective tape).
- Sand down the edges of the PMMA and de-bur to make sure the material will sit level on the CNC
- (Have someone operate the CNC for you using the included G-Code files along with your modifications)
- Plan ahead to reserve the crushinator (hot press)

<p align="center">
  
</p>
<p align="center">Freshly milled devices ready for bonding</p>

### Bonding

- Once beautifully-well cut, clean the device with IPA, Methanol, DI, and nitrogen dry. Then place in the cleanroom ovens overnight (70°C)
- The next day, prep for bonding both pieces of PMMA
- Set the Hot Press to 85°C and let it heat up
- Collect two of metal plates, red rubber sheets, and clear teflon sheets that are larger than the PMMA device. You will then sandwich the device between these three layers
- Go into `Manual` mode and configure these Hot Press settings:
  +  pressure equal to the surface area of the PMMA device (in inches) times 500 lbs/sq. in
  + 35% pump speed
  + (the time will be 15 minutes)
- Once the hot press is nearly hot enough, put both pieces of the PMMA device face up in the UV-Ozone for 10 minutes
- Place the PMMA device together and carefully align it inside the sandwich of Metal/Rubber/Teflon/Device/Teflon/Rubber/Metal inside the crushinator
- Press for fifteen minutes
- Once done, you will need to cool the device (**important**). If not, the device will warp irreparably
  + First turn the set temperature from 85°C down to about 20°C or so (this will allow you to monitor the temperature in real time)
  + In Manual mode, tun on the water cooling setting
  + Wait about ten minutes until the crushinator registers a temperature close to room temperature (keep in mind that the chip will be hotter than the displayed temperature)
  + Purge the water cooling system with air (in manual, turn off water and turn on air)
  + Remove the bonded chip and inspect under the microscope, if it looks good cover the needleports with blue tape. Place in a petri dish and let sit at room temperature over night for the material stresses to relax

### Needle Press

- This is tricky and you will need to ask for someone to demonstrate the process. You will attach the fresh needle to the drill press and carefully insert it into the PMMA device. I used 22 gauge needles
- Tips
  + If the needle touches the bottom plate of the PMMA device, your inlet will clog
  + Go slowly and accurate or you make create spiderweb cracks around the inlet. Small ones are okay and can be covered with epoxy, but will limit the life of the device
  + Make sure the needle is straight in the chuck (you can test by manually spinning the drill)
  + A trick from Eric, while rotating the needle, drag it along a piece of sand paper to round off the tip of the needle
  + With the dedicated microscope, align both the needle and port with the focal point
- Once the needles are pressed, cover the connection with epoxy for better stability and attach your fluidic connections

<p align="center">
  
</p>
<p align="center">Pressing needles while using the USB microscope (replaced in favor of the dedicated microscope once Dr. Eric Kendall fixed the mounting hardware</p>

## Evolution of the PMMA Devices

After some success with the PDMS devices, I designed a simple PMMA device that was 50mm x 50mm and nice large features that were easy to mill. The most important feature was the droplet generator section which was 150 µm  (width) by 40 µm (depth). After testing the device to produce agarose droplets, I moved onto producing agarose beads. I faced far fewer clogging issues and generated far more consistently sized beads for longer. I continued to extend the device capabilities by adding a heating element as shown in `8_Turtlebot` folder.

<p align="center">
  
</p>
<p align="center">Early PMMA Device</p>

<p align="center">
  
</p>
<p align="center">
  
</p>
<p align="center">Water Droplet Production</p>

Realizing one of the major drawbacks was beads colliding and coalescing together, especially around the exit port, I designed the chip to exit directly into solution (see video: `RoomTempAgaroseDropletGeneration.mp4` and `FirstDualHeatStage.mp4`). Additionally, the chip was longer to allow the beads to be cooled while still on the PMMA device.

<p align="center">
  
</p>
<p align="center">Extended channel length variation</p>

<p align="center">
  
</p>
<p align="center">The longer PMMA Device</p>

<p align="center">
  
</p>
<p align="center">
  
</p>
<p align="center">Slight after-market modification to collect the beads</p>

<p align="center">
  
</p>
<p align="center">
  
</p>
<p align="center">Final version with cutout to submerge in a mini petri-dish</p>

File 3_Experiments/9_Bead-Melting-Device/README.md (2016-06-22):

# Melter (single heat stage version of the TurtleBot)

The melter is a single heat stage from the Turtle bot, so for the 3D printed parts, `see 6_CAD-Files`, for the electronics, see `5_Electronic-Diagrams`, and for the code and operation instructions, see `4_Software/MML-HeatStage`. To see the issues described in packing the bead bed, see the video `FailedAgarosePacking.mp4`.

<p align="center">
  
</p>
<p align="center">
  
</p>
<p align="center">The full Melter setup</p>

<p align="center">
  
</p>
<p align="center">Close up of the bead bed chip as it was melted</p>

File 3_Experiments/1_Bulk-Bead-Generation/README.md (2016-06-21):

# Bulk Bead Generation

The most simple approach to agarose droplet generation:

**1% Agarose Mixture:**

- Using a 5ml glass beaker add 5g of DI
- Weigh out 0.05g of LMP agarose onto wax paper
- Microwave the glass beaker and water twice for 20 second intervals
- Add the agarose powder and microwave one additional time of 20 seconds
- If not completely dissolved mix with a pasteur pipette
- Make sure to keep warm until ready for use (can place in oven)

**Silicone Oil (or Mineral Oil) with 2% w/w Surfactant (Span 80)**

- Add a specific mass of surfactant to oil
- The tricky part is mixing. You don't want to introduce bubbles, so I just mixed with a plastic pasteur pipette
- Additionally the span 80 is very viscous, so I would prefer to dilute it to a first container with my chosen oil

<p align="center">
  
  <!-- <figcaption style="text-align: cener;">Whiteboard sketch of the bulk bead generation process</figcaption> -->
</p>

<p align="center">Whiteboard sketch of the bulk bead generation process</p>

From a pipette or capillary, drip the hot agarose mixture into a beaker of silicone oil. Additionally, you can place the beaker of oil into an ice bath to quickly cool the beads.

<p align="center">
  
  <!-- <figcaption style="text-align: cener;">Beads in oil after following the above process</figcaption> -->
</p>

<p align="center">Beads in oil after following the above process</p>

<p align="center">
  
  <!-- <figcaption style="text-align: cener;">The beads varied greatly, but were around 2.5 mm (0.1 in) in diameter</figcaption> -->
</p>

<p align="center">The beads varied greatly, but were around 2.5 mm (0.1 in) in diameter</p>

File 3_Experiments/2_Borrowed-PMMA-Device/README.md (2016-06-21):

# Inherited PMMA Chip Test

Using chips left over from KJ's work, I setup a heated platform on a hot plate and collected the beads in an ice bath. The experiment went very well and proved very promising. After this success, I attempted to make the beads smaller and to produce greater quantities using PDMS devices.

<p align="center">
  
  <!-- <figcaption style="text-align: center;">The complete setup</figcaption> -->
</p>
<p align="center">
  
</p>
<p align="center">The complete setup</p>

<p align="center">
  
  <!-- <figcaption style="text-align: center;">A metal plate was used to maintain a more constant temperature</figcaption> -->
</p>
<p align="center">A metal plate was used to maintain a more constant temperature</p>

<p align="center">
  
  <!-- <figcaption style="text-align: center;">The device channel was 300µm wide</figcaption> -->
</p>
<p align="center">The device channel was 300µm wide</p>

<p align="center">
  
  <!-- <figcaption style="text-align: center;">The beads were collected in a petri dish at room temperature after traveling the length of the exit tube</figcaption> -->
</p>
<p align="center">The beads were collected in a petri dish at room temperature after traveling the length of the exit tube</p>

<p align="center">
  
  <!-- <figcaption style="text-align: center;">The generated beads were roughly ~100µm in diameter (the scale bar is 1mm)</figcaption> -->
</p>

<p align="center">The generated beads were roughly ~100µm in diameter (the scale bar is 1mm)</p>

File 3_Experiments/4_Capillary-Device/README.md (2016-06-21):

# Capillary Device

In an attempt to make even smaller agarose beads, I built a simple coflow droplet generator using a glass capillary inside of a teflon outer tube. I struggled with clogging and quickly moved onto PDMS devices using a mask provided by Renee Hood.

<p align="center">
  
</p>

<p align="center">
  
</p>

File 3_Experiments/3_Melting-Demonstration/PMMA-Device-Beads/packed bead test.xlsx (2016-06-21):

FileName | Time (ms) | Z Pos | X Pos | Y Pos | ROI ID | ROI Area | ROI Mean Intensity | ROI Min Intensity | ROI Max Intensity | ROI Sum Intensity | ROI StDev Intensity | ROI Signal/Background | Binary Area | Binary Mean Intensity | Binary Min Intensity | Binary Max Intensity | Binary Sum Intensity | Binary StDev Intensity | Binary Signal/Background | Area Fraction | Unit | Channel
packed bead test 2.nd2 | 2873019.369 | 0 | 0 | 0 | 1 | 2073615.159 | 100.311321 | 41 | 142.666667 | 244559 | 16.321792 | 1.100629 | 0 | N/A | N/A | N/A | N/A | N/A | N/A | 0 | µm | RGB
packed bead test 2.nd2 | 2873019.369 | 0 | 0 | 0 | 2 | 3317103.822 | 172.084103 | 159.666667 | 175.333333 | 671128 | 1.455837 | 1.100629 | 0 | N/A | N/A | N/A | N/A | N/A | N/A | 0 | µm | RGB
packed bead test 2 after.nd2 | 4445995.369 | 0 | 0 | 0 | 1 | 2073615.159 | 152.242275 | 89.666667 | 167.333333 | 371166.6667 | 7.862117 | 1.876404 | 0 | N/A | N/A | N/A | N/A | N/A | N/A | 0 | µm | RGB
packed bead test 2 after.nd2 | 4445995.369 | 0 | 0 | 0 | 2 | 3317103.822 | 167.786923 | 153 | 174.666667 | 654369 | 3.514626 | 1.876404 | 0 | N/A | N/A | N/A | N/A | N/A | N/A | 0 | µm | RGB

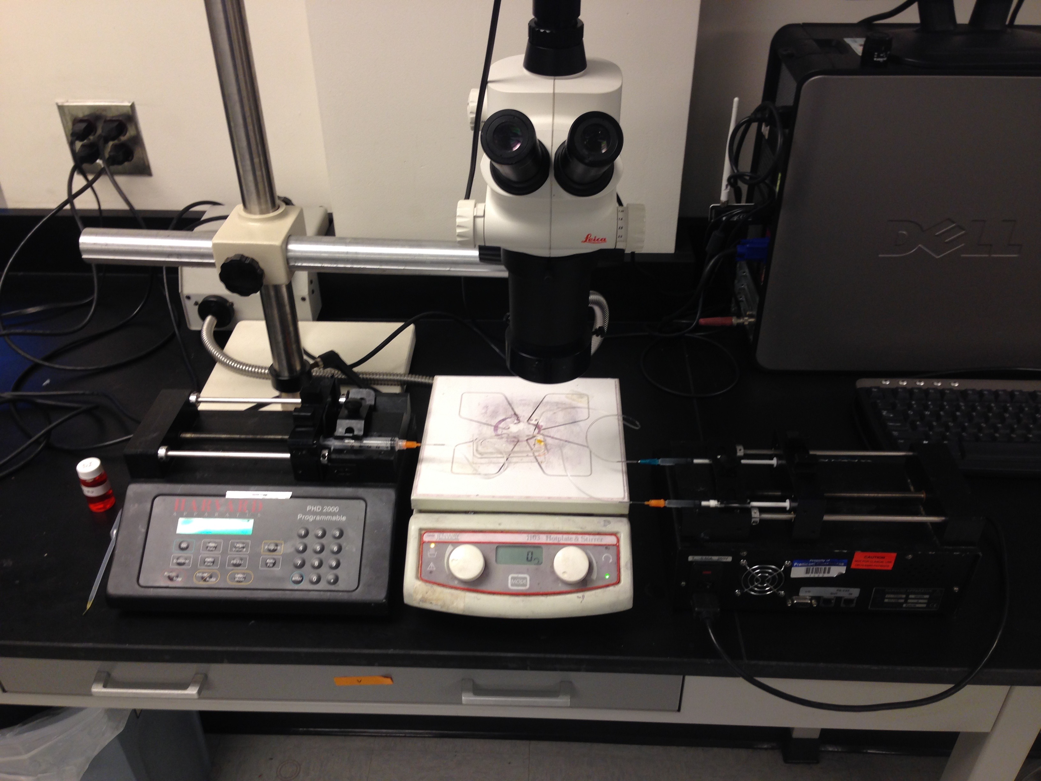
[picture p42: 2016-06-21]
3_Experiments/5_PDMS-Devices/imgs/vacuum/1_wide.jpg

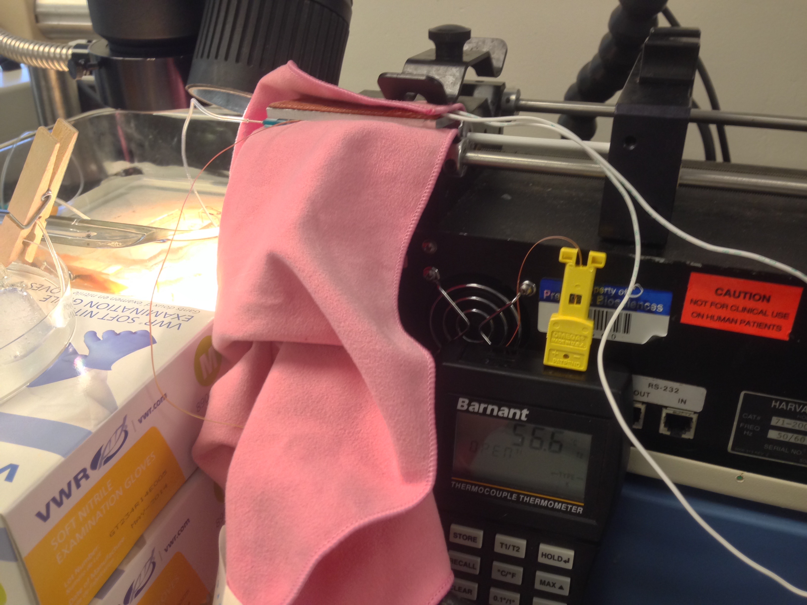
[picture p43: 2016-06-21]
3_Experiments/5_PDMS-Devices/imgs/pressure/1_heatedsyringe.jpg

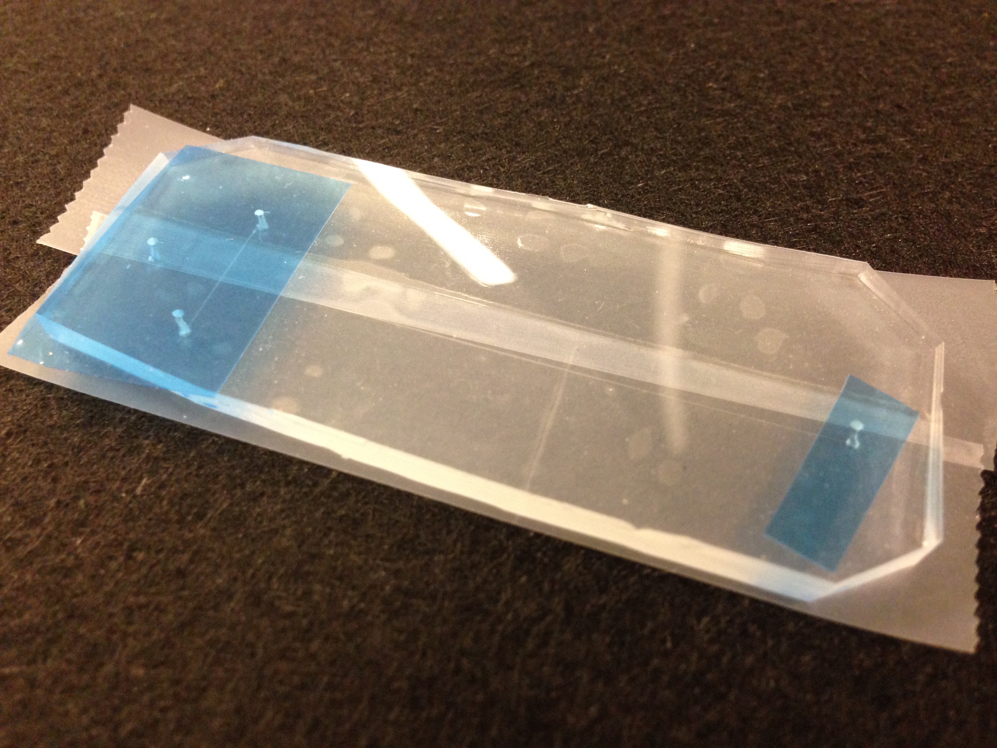
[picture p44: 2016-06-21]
3_Experiments/5_PDMS-Devices/imgs/protocol/tapefordays.jpg

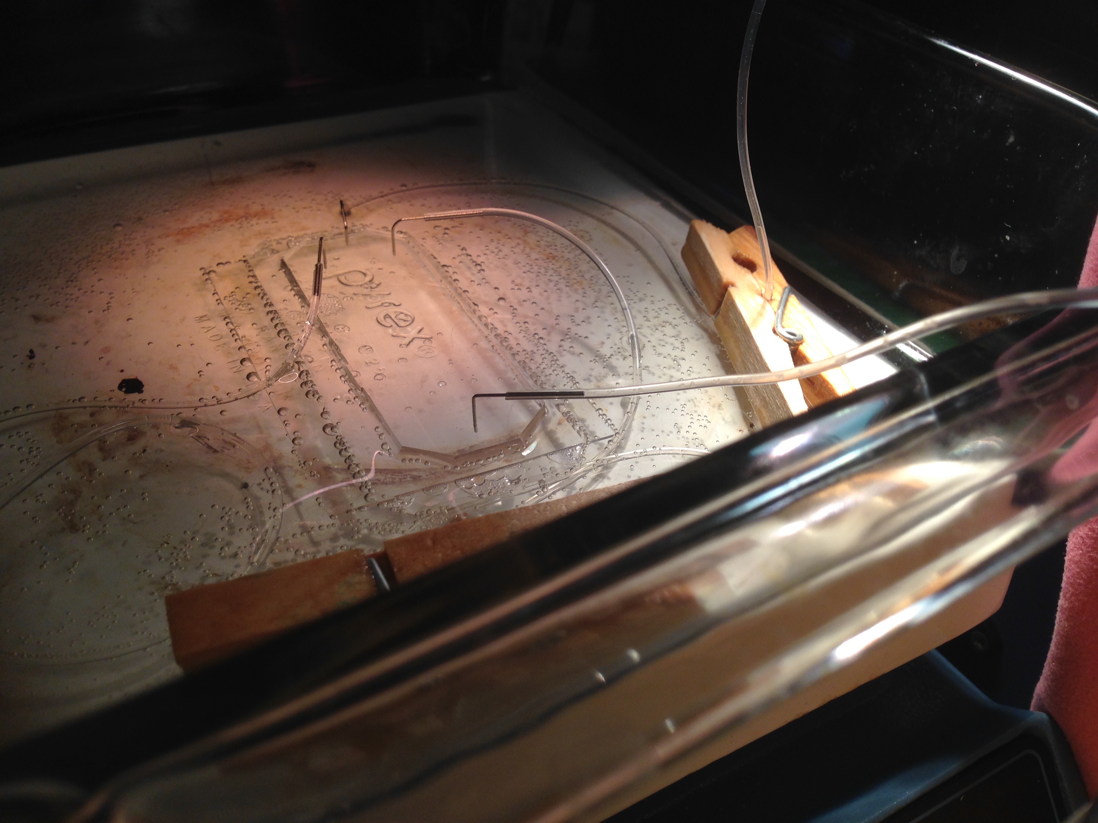
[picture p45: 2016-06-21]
3_Experiments/5_PDMS-Devices/imgs/pressure/1_submergedchip.jpg

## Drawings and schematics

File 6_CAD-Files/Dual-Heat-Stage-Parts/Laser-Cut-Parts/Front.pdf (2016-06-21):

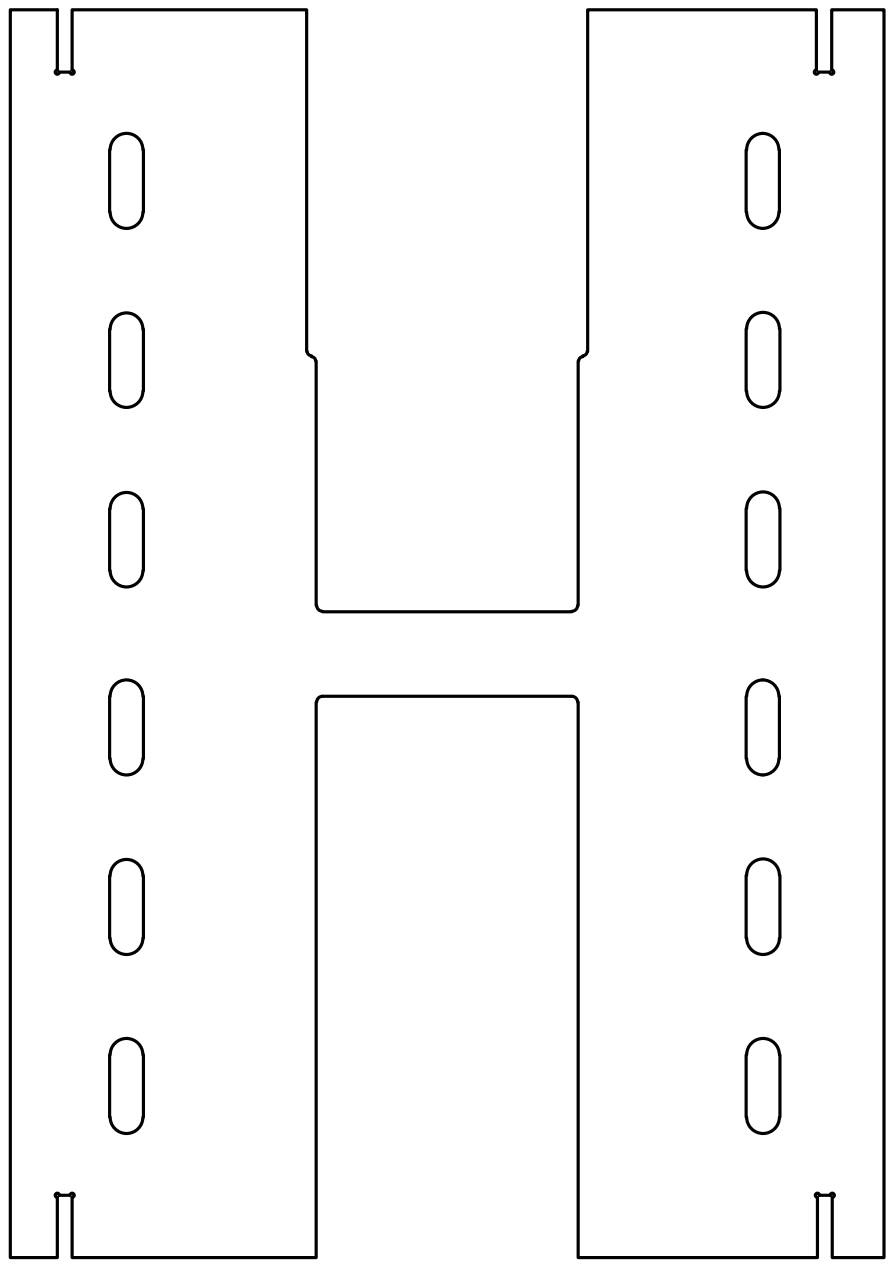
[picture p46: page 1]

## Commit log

2016-06-21 condensed experiment list
    [packed bead test.xlsx]
2016-06-21 New MML-HeatStage Submodule
2016-06-25 Tested SocketIO app
2016-07-02 Removed MML-Heatstage Submodule
2016-07-02 Re-added submodule MML-HeatStage
